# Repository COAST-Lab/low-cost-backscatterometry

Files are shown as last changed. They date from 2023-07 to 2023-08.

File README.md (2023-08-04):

# Documentation

•	The goal is to create a device that measures turbidity in a water sample.  Components include: Particle Argon microprocessor attached via stacking headers to an Adalogger FeatherWing (which includes a PCF 8523 RTC and SD card slot-note there must always be a battery in the coin battery holder, even if its a dead one, or the device will lose track of time), Adafruit AW9523 LED driver, Adafruit 7341 sensor, IR LED, cuvette holder, light blocking cap, 12.5mm x 12.5mm x 45mm (outer dimension) cuvette, and housing.  The LED and sensor must be perpindicular to each other, which the cuvette holder is designed to accomodate. Light from the LED enters the sample, and after striking any turbidity-causing particles in the water sample, bounces off and is read by the sensor.  The more light that reaches the sensor, the higher the turbidity.

•	The CAD file for the cuvette holder is in the CAD directory, and is called "cuvette holder v3", which is the most up-to-date version.  The light blocking cap that goes with it is in the same directory.  Directions for how to assemble the device are also in the same directory, and is called "Cuvette Holder Notes and Specifications".  If printing a new cuvette holder, be advised that the inside walls of the cavities may need to be sanded/shaved, or their intended pieces may not fit.

• The housing for the device will need to be ordered.

•	 To flash the LED, there is a program in the following directory: Firmware/Turbidity_Argon.  As of 4 Aug, 2023, there are two versions: Turbidity_v3 and Turbidity_v4.  Both flash an IR LED for a set time interval while bright, and flashes for a set time interval while dim.  We do not want the LED to turn off completely, which is why the LED needs to switch back and forth from bright to dim.  This is a workaround for the sensor reading negative values, which will display as “0”.  During each interval, the AS7341 will take light measurements and record them to an SD card, and it will say whether the reading was during a bright or a dim interval.

•	Turbidity_v3 is a workable code, but just needs to be fine-tuned and condensed (see next steps).  Turbidity_v4 is an attempt to correct the issues in turbidity_v3, but is less usable than Turbidity_v3, and is a work in progress.

•	If sample collection and readings are needed before Turbidity_v4 is complete, then use Turbidity_v3.  Despite the issues with that version, it has fewer issues and does everything that is needed.

•	If testing Turbidity_v3 or Turbidity_v4, you can cover the sensor when the light goes dim, and uncover when the light goes bright; this will reflect in the readings.

•	The ATIME is set to 59, and ASTEP is set to 599, and Gain is set to AS7341_GAIN_4X, per Bob Brewin’s recommendation.  Using the equation: integration time = (ATIME + 1) x (ASTEP+1) x 2.78 µs, this leads to an integration time of 100.08 ms.  Integration time is the amount of time the sensor measures light, and the gain is the sensitivity of the sensor.  

•	Be advised: When flashing the program at each of the gain settings, it will not save to the SD card as that gain, it will only save as a number that increases by 1 as you increase to the next gain setting.  For example, the .5 setting outputs/saves to SD card as 0, and just increases by 1 for the next setting up.  Here it is, formatted as (Gain setting -- what it saves to the card as):

    o	AS7341_GAIN_0_5x -- 0
  
    o	AS7341_GAIN_1x -- 1
    
    o	AS7341_GAIN_2x -- 2
    
    o	AS7341_GAIN_4x -- 3
    
    o	AS7341_GAIN_8x -- 4
    
    o	AS7341_GAIN_16x -- 5
    
    o	AS7341_GAIN_32x -- 6
    
    o	AS7341_GAIN_64x -- 7
    
    o	AS7341_GAIN_128x -- 8
    
    o	AS7341_GAIN_256x -- 9
    
    o	AS7341_GAIN_512x – 10

•	In the code, the LED intensities (bright and dim) are listed as variables, which are: LEDbright and LEDdim.  The bright setting is 250 and the dim setting is 1 (this is to clearly distinguish between the bright and dim settings).  These are arbitrary; feel free to adjust those numbers as needed when using the IR LED.  

• For both versions, the time stamp includes: year, month, day, hour, minute, second, and millisecond.  Be advised that this is not synced up with the RTC (the RTC cannot process units smaller than a second, while the Argon records the time since it was last reset in milliseconds), however it is useful to determine the timing of the intervals.  Also, in the code, be advised that the serial print and fileprint record the timestamps differently (HH:MM:SS.mmm and HH:MM:SS:mmm, respectively).  If you try to format the fileprint timestamp as HH:MM:SS.mmm, it will not record the hours for whatever reason.  

•	Optical measurements are complete.  This process involved placing the sensor in a box with a 1-inch diameter hole, with the sensor 5 inches away from the hole.  The inside of the box was black.  Outside of the box, there was a posterboard mounted at a 45 degree angle to the hole, and reflects light into the hole.  The following measurements were needed: while the posterboard was facing the sun (or flat on the ground) during a sunny day; shortly after the first measurement, but with a square or disk completely shadowing the posterboard; and indoors with the hole covered.  For light and shadow runs, two 1-minute runs were conducted and recorded, and for the dark, one 1-minute run was conducted.  Note that for the dark measurements, in order to get any reading at all, the gain had to be increased to x512, (which is the highest gain), and the integration time had to be increased to 1000 ms (this required the ATIME to be set to 103-the highest it’ll let you go, and an ASTEP of 3457).  Even then, we had to gradually let more and more light into the box by slowly removing the cover.  The measurements were averaged, and given to Alan Holmes for processing.  The measurements collected can be found in the following directory: Data_Analysis/Data/27Jul_Turbidity_Optical_Calibration_Data.xlsx.  Alan’s results are in: Data_Analysis/Data/WilmingtonResult-072723.xlsx (use the numbers in yellow). 

•	In addition to the runs above, there was an additional dark counts run, this time with enough light so that the average ADU for the NIR was ~100, per Alan’s recommendation.  This can be found in the same Data folder that the other optical files are in, and is named “100ADU_Dark_2023_Jul_28_1104.csv.

•	In the Firmware directory, there is a program called Hawkeyewavelengths-this just cycles the Argon’s onboard LED through all the wavelengths in the Hawkeye satellite.  Be advised that running this will move control of the Argon to the user, and it cannot be used for other applications unless control is returned to the Argon.  To return control to the Argon, simply flash the Returncontroltoargon program (be sure to flash while the on-board LED is on!).

# Next Steps

•	Condense the coding into functions.  Right now Turbidity_v4 is condensed into functions, but the timing is off-it’ll sometimes record bright intervals (250) as dim (1), and vice versa.  Also it stays on an interval for a lot longer.  Turbidity_v3 does not have functions and is bulkier, but does not have these issues either.

•	The number of consecutive samples at a given LED intensity appears to be variable. Sometimes it's two, sometimes four. We'd need that to be a fixed value for future analyses. Ideally a variable that can be set just like the intensity itself.  

•	Assemble the turbidity device.  The entire setup is on two breadboards connected together, but recommend finishing the coding before disassembly, since this setup already has a working RTC.

•	Order the housing for the turbidity device.

•	Once the turbidity meter is assembled, the next step is calibration.  Google ISO 7027 and EPA 180.1 for reference, as these are the standards to abide by.  

•	After calibration, the device will be ready to take measurements.

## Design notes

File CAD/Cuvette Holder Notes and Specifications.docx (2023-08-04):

Cuvette Holder, Version 3 Notes and Specifications

- Cuvette holder v2 is designed to hold a 12.5mm x 12.5mm x 45mm (outer dimensions) cuvette, with the AS7341 sensor, AW9523 LED driver, and Particle Argon/RTC combo mounted directly on the cuvette holder.
- The cavity that holds the cuvette is 30mm deep, leaving 15mm at the top to easily grab and swap out.
- The holes for the sensor and LED light are centered vertically and 15mm below the top of the cuvette holder.
- Place the AS7341 into the cavity with the same dimensions, with the sensor facing towards the inside of the cuvette holder, and text should be right side up. Note there is also a small notch in the upper right corner to accommodate the on-board LED. Also note there is a small portion around the center of the cavity that is raised-this surrounds the sensor and blocks out light coming from the LED.
- Place the AW9523 LED driver in the cavity with the same dimensions, with its main components on “top”, facing the user. The LED will need to be mounted on the “bottom” side of the LED driver (pinout 0), facing towards the inside of the cuvette holder. You may need to adjust the position of the LED in order to get it to fit. The large screw hole right above pinout 0 will need to be plugged up so it won’t let light through.
- The screw holes on the cuvette holder were left out, so the user has more flexibility on screw size, and can easily drill holes in the cuvette holder, or just tape or glue the parts to the cuvette holder. On the AS7341, the upper right corner should remain unscrewed, as it will get very close to the screw from the upper left corner screw of the LED driver.
- The cuvette holder is also designed to have a light blocking cap placed over the cuvette. This can be found in the same directory as the cuvette holder file.
- On one side of the cuvette holder are two grooves. Place the stacking headers from the Argon+RTC in the grooves, then secure to the cuvette holder, for example with electrical tape.
- Place the cuvette with sample water into the cuvette cavity, which is on the top of the cuvette holder.
- Place the light blocking cap over the cuvette and wiggle it in until snug.
- Note that the inside walls of the cavities may need to be sanded or shaved in order to accommodate their intended components.

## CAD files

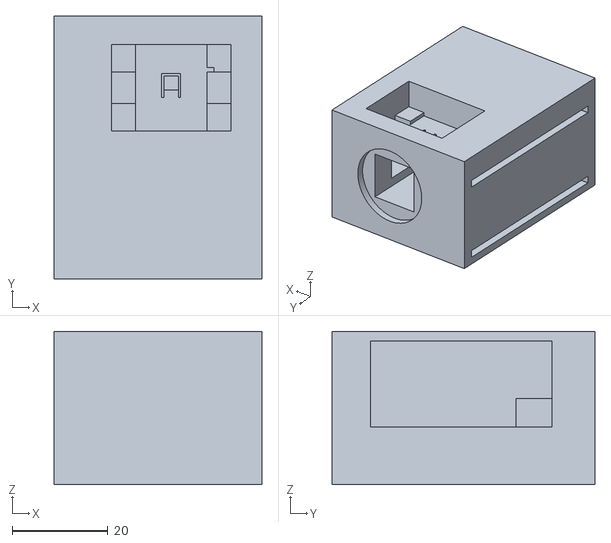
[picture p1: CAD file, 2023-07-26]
CAD/Cuvette Holder v3.stl
43.5 x 55.0 x 32.0

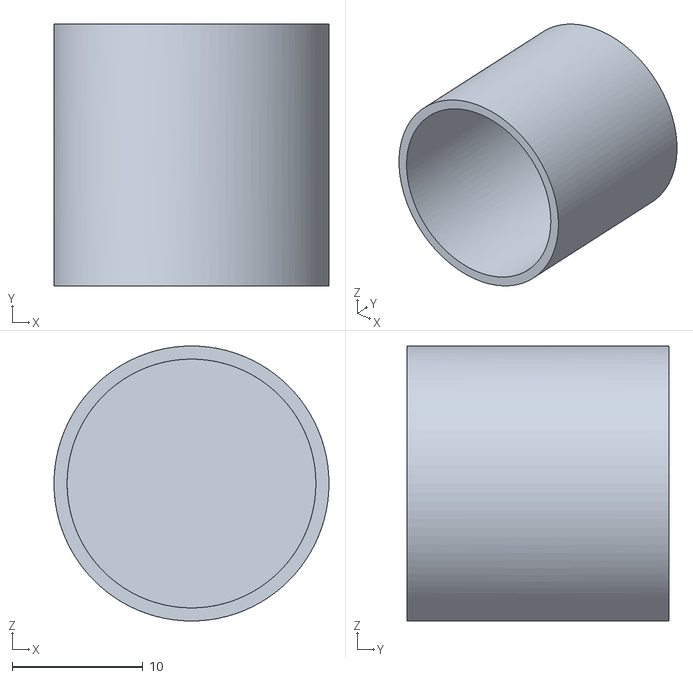
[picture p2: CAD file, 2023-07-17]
CAD/Light_Blocking_Cap.stl
21.0 x 20.0 x 21.0

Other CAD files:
CAD/Cuvette Holder v3.ipt
CAD/Light_Blocking_Cap.ipt

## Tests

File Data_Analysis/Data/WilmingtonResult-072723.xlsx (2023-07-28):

Wilmington Data of 7/27/20923
Alan Holmes
Gain was 4X
Integration time was 100 milliseconds
Measurements captured at 13:30 on Thursday July 27, 2023
74.69 | solar elevation angle in degrees
 |  |  |  | Expected | Derived
 |  |  |  | Sensor | Sensor
 |  |  |  | Irradiance | Calibration
 |  |  |  | in | in ADU Per | From
 | ADU | ADU | ADU | microwatts | microwatt | Data
 | AVERAGE | Shadow | Diff | per cm^2 | per cm^2 | Sheet
F1 415nm | 168.9791667 | 14.60416667 | 147.4166667 | 25.7 | 5.74 | 56.1 | (at gain of 512X) | (at 4X this would be 119th as much, or 0.47)
F2 445nm | 250.8125 | 19.77083333 | 220.5208333 | 29.0 | 7.59 |  | (and Tint of 100ms)
F3 480nm | 350.625 | 22.6875 | 310.6458333 | 47.4 | 6.56
F4 515nm | 434.5208333 | 25.8125 | 384.8958333 | 50.1 | 7.68
F5 555nm | 459.8333333 | 24.9375 | 410.1666666 | 50.8 | 8.08
F6 590nm | 514.25 | 25.79166667 | 461.5208333 | 51.2 | 9.02
F7 630nm | 681.1041667 | 30.83333333 | 614.4166666 | 65.3 | 9.41
F8 680nm | 669.6458333 | 31.8125 | 607.4583333 | 64.6 | 9.40
NIR | 698.8 | 52.25 | 643.6875 | 82.2 | 7.83 | 52 | (at gain of 128x) | (at 4X this would be 30.7th as much, or 1.69)
 |  |  |  | (From | (at 4X and 100 ms T-int)
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

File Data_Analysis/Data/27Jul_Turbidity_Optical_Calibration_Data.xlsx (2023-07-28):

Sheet: Light Measurements 1
Date | 2023/7/27 (Thursday)
ASTEP: | 599
ATIME: | 59
GAIN: | AS7341_GAIN_4X
INTEGRATION TIME: | 100.08 ms
APERATURE FACING: | 219° SW
 | Time | F1 415nm | F2 445nm | F3 480nm | F4 515nm | F5 555nm | F6 590nm | F7 630nm | F8 680nm | Clear | NIR
 | 13:27:20 | 169 | 251 | 351 | 435 | 461 | 516 | 684 | 672 | 2733 | 699
 | 13:27:21 | 170 | 252 | 352 | 436 | 461 | 516 | 684 | 672 | 2733 | 700
 | 13:27:22 | 170 | 252 | 352 | 436 | 462 | 516 | 684 | 673 | 2734 | 700
 | 13:27:24 | 169 | 251 | 352 | 436 | 461 | 515 | 683 | 672 | 2730 | 699
 | 13:27:25 | 169 | 251 | 351 | 436 | 461 | 516 | 683 | 672 | 2730 | 699
 | 13:27:26 | 169 | 251 | 351 | 435 | 461 | 516 | 683 | 672 | 2729 | 699
 | 13:27:27 | 169 | 251 | 352 | 436 | 462 | 516 | 684 | 672 | 2733 | 700
 | 13:27:29 | 170 | 252 | 352 | 436 | 461 | 515 | 683 | 671 | 2728 | 699
 | 13:27:30 | 170 | 252 | 352 | 436 | 462 | 516 | 684 | 672 | 2733 | 701
 | 13:27:31 | 170 | 252 | 352 | 437 | 462 | 517 | 685 | 673 | 2738 | 702
 | 13:27:33 | 170 | 252 | 352 | 436 | 462 | 517 | 685 | 674 | 2738 | 702
 | 13:27:34 | 170 | 252 | 353 | 437 | 462 | 517 | 685 | 673 | 2734 | 702
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

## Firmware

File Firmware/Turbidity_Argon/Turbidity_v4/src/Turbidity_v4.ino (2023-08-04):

//This program monitors light while giving a time stamp and recording both
//basic counts and raw values to an SD card

#include <Adafruit_AS7341.h>
#include <Adafruit_AW9523.h>
#include "RTClibrary.h"
#include <SdFat.h>

Adafruit_AS7341 as7341;
Adafruit_AW9523 aw;
RTC_PCF8523 rtc;
File myFile;
SdFat SD;

char daysOfTheWeek[7][12] = {"Sunday", "Monday", "Tuesday", "Wednesday", "Thursday", "Friday", "Saturday"};
const int SD_CHIP_SELECT = D5;
uint8_t LedPin = 0;
int LEDbright = 250;  // adjust this number as needed
int LEDdim = 1;       // adjust this number as needed

SYSTEM_THREAD(ENABLED);
SYSTEM_MODE(SEMI_AUTOMATIC);

void setup() {
  Serial.begin(9600);

  // Wait for communication with the host computer serial monitor
  while (!Serial) {
    delay(1);
  }
  
  if (!as7341.begin()){
    Serial.println("Could not find AS7341");
    while (1) { delay(10); }
  }
  
  // use ATIME of 103, ASTEP of 3457, and GAIN of 512x for dark counts during optical calibration
  as7341.setATIME(59);      
  as7341.setASTEP(599);
  as7341.setGain(AS7341_GAIN_4X);

  if (! rtc.begin()) {
    Serial.println("Couldn't find RTC");
    while (1);
  }

  if (! rtc.initialized()) {
    Serial.println("RTC is NOT running!");
    // following line sets the RTC to the date & time this sketch was compiled
    // rtc.adjust(DateTime(F(__DATE__), F(__TIME__)));
    // This line sets the RTC with an explicit date & time, for example to set
    // January 21, 2014 at 3am you would call:
    // rtc.adjust(DateTime(2014, 1, 21, 3, 0, 0));
  }

  if (! aw.begin(0x58)) {
    Serial.println("AW9523 not found? Check wiring!");
    while (1) delay(10);  // halt forever
  }

  Serial.println("AW9523 found!");
  aw.pinMode(LedPin, AW9523_LED_MODE);

  SD.begin(SD_CHIP_SELECT);
 
  File file = SD.open("data.csv", FILE_WRITE);

  if (file) {
    file.print("ASTEP:");
    file.print(',');
    file.println(as7341.getASTEP());
    file.print("ATIME:");
    file.print(',');
    file.println(as7341.getATIME());
    file.print("GAIN (check table):");
    file.print(',');
    file.println(as7341.getGain());
    // 0.5x records as 0, 1x records as 1, 2x records as 2, 4x records as 3, 
    // 8x records as 4, 16x records as 5, 32x records as 6, 64x records as 7,
    // 128x records as 8, 256x records as 9, 512x records as 10.
    file.println(" ");
    file.println("LED Intensity,Date,Time,Type,F1 (Basic),F2 (Basic),F3 (Basic),F4 (Basic),F5 (Basic),F6 (Basic),F7 (Basic),F8 (Basic),Clear (Basic),NIR (Basic),Type,F1 (Raw),F2 (Raw),F3 (Raw),F4 (Raw),F5 (Raw),F6 (Raw),F7 (Raw),F8 (Raw),Clear (Raw),NIR (Raw)"); // Headers
    file.close();
  } else {
    Serial.println(F("Error opening file!"));
  }
}

void loop() {


  // put your main code here, to run repeatedly:

  //File file = SD.open("data.csv", FILE_WRITE);
  //DateTime now = rtc.now();

  // Switch LED intensity to bright.

  unsigned long currentTime = millis();  // Current time in milliseconds
  unsigned long onTime = 500;  // 1 second on time
  unsigned long offTime = 500;  // 1 second off time

  // Calculate the time elapsed since the start of the loop
  unsigned long elapsedTime = currentTime % (onTime + offTime);



  bool isLedOn = (elapsedTime < onTime);
  aw.analogWrite(LedPin, isLedOn ? LEDbright : LEDdim); // Turn LED on or off
  // aw.analogWrite(LedPin, 250);

  //delay(100);

  serialprintresults();
  
  //save data to SD card

  // if (file) {

    //  print readings
     
    // file.print("LED BRIGHT");
  
    
    fileprintresults();
  // }

  // else {
  //  Serial.println(F("Error opening file!"));
  //}

  //delay(250);

//  Switch LED intensity to dim.



  bool isLedOff = (elapsedTime < offTime);
  aw.analogWrite(LedPin, isLedOff ? LEDdim : LEDbright);
  // aw.analogWrite(LedPin, 1);

  //delay(100);

  serialprintresults();
  
  //save data to SD card
  
  //if (file) {

    //  print readings
     
    //file.print("LED DIM");

  fileprintresults();



//else {
  //  Serial.println(F("Error opening file!"));
 // }

 // delay(250);

}

void serialprintresults() 
{

DateTime now = rtc.now();
unsigned long decimalseconds_to_record = (millis() % 1000)/1; //the divided by 1 has to stay, otherwise the program gets stuck during serial monitor!

Serial.print("LED INTENSITY:");
  Serial.print(" ");
  Serial.println(LEDbright);
  Serial.println();
  Serial.print(now.year(), DEC);
  Serial.print('/');
  Serial.print(now.month(), DEC);
  Serial.print('/');
  Serial.print(now.day(), DEC);
  Serial.print(" (");
  Serial.print(daysOfTheWeek[now.dayOfTheWeek()]);
  Serial.print(") ");
  Serial.print(now.hour(), DEC);
  Serial.print(':');
  Serial.print(now.minute(), DEC);
  Serial.print(':');
  Serial.print(now.second(), DEC);
  Serial.print('.');
  Serial.print(decimalseconds_to_record, DEC);
  Serial.println();

  uint16_t readings[12];
  float counts[12];

    if (!as7341.readAllChannels(readings)){
    Serial.println("Error reading all channels!");
    return;
  }

  for(uint8_t i = 0; i < 12; i++) {
    if(i == 4 || i == 5) continue;
    // we skip the first set of duplicate clear/NIR readings
    // (indices 4 and 5)
    counts[i] = as7341.toBasicCounts(readings[i]);
  }

  Serial.print("F1 415nm : ");
  Serial.print(counts[0]);
  Serial.print("  ");
  Serial.print("Raw Value : ");
  Serial.println(readings[0]);
  Serial.print("F2 445nm : ");
  Serial.print(counts[1]);
  Serial.print("  ");
  Serial.print("Raw Value : ");
  Serial.println(readings[1]);
  Serial.print("F3 480nm : ");
  Serial.print(counts[2]);
  Serial.print("  ");
  Serial.print("Raw Value : ");
  Serial.println(readings[2]);
  Serial.print("F4 515nm : ");
  Serial.print(counts[3]);
  Serial.print("  ");
  Serial.print("Raw Value : ");
  Serial.println(readings[3]);
  Serial.print("F5 555nm : ");

  // again, we skip the duplicates  

  Serial.print(counts[6]);
  Serial.print("  ");
  Serial.print("Raw Value : ");
  Serial.println(readings[6]);
  Serial.print("F6 590nm : ");
  Serial.print(counts[7]);
  Serial.print("  ");
  Serial.print("Raw Value : ");
  Serial.println(readings[7]);
  Serial.print("F7 630nm : ");
  Serial.print(counts[8]);
  Serial.print("  ");
  Serial.print("Raw Value : ");
  Serial.println(readings[8]);
  Serial.print("F8 680nm : ");
  Serial.print(counts[9]);
  Serial.print("  ");
  Serial.print("Raw Value : ");
  Serial.println(readings[9]);
  Serial.print("Clear    : ");
  Serial.print(counts[10]);
  Serial.print("  ");
  Serial.print("Raw Value : ");
  Serial.println(readings[10]);
  Serial.print("NIR      : ");
  Serial.print(counts[11]);
  Serial.print("  ");
  Serial.print("Raw Value : ");
  Serial.println(readings[11]);
  Serial.print("  ");
  Serial.println();
}

void fileprintresults() 
{

File file = SD.open("data.csv", FILE_WRITE);
DateTime now = rtc.now();
unsigned long decimalseconds_to_record = (millis() % 1000)/1; //the divided by 1 has to stay, otherwise the program gets stuck during serial monitor!

 uint16_t readings[12];
  float counts[12];

    if (!as7341.readAllChannels(readings)){
    Serial.println("Error reading all channels!");
    return;
  }

  for(uint8_t i = 0; i < 12; i++) {
    if(i == 4 || i == 5) continue;
    // we skip the first set of duplicate clear/NIR readings
    // (indices 4 and 5)
    counts[i] = as7341.toBasicCounts(readings[i]);
  }

if (file) {

  unsigned long currentTime = millis();  // Current time in milliseconds
  unsigned long onTime = 500;  // 1 second on time
  unsigned long offTime = 500;  // 1 second off time

  // Calculate the time elapsed since the start of the loop
  unsigned long elapsedTime = currentTime % (onTime + offTime);

  bool isLedOn = (elapsedTime < onTime);

  //delay(100);

  file.print(isLedOn ? LEDbright : LEDdim);
    file.print(',');
file.print(now.year(), DEC);
    file.print('/');
    file.print(now.month(), DEC);
    file.print('/');
    file.print(now.day(), DEC);
    file.print(" (");
    file.print(daysOfTheWeek[now.dayOfTheWeek()]);
    file.print(") ");
    file.print(',');
    file.print(now.hour(), DEC);
    file.print(':');
    file.print(now.minute(), DEC);
    file.print(':');
    file.print(now.second(), DEC);
    file.print(':');
    file.print(decimalseconds_to_record, DEC);
    file.print(',');
    file.print("BASIC COUNTS");
    file.print(',');
    file.print(counts[0]);
    file.print(',');
    file.print(counts[1]);
    file.print(',');
    file.print(counts[2]);
    file.print(',');
    file.print(counts[3]);
    file.print(',');
    file.print(counts[6]);
    file.print(',');
    file.print(counts[7]);
    file.print(',');
    file.print(counts[8]);
    file.print(',');
    file.print(counts[9]);
    file.print(',');
    file.print(counts[10]);
    file.print(',');
    file.print(counts[11]);
    file.print(',');
    file.print("RAW VALUES");
    file.print(',');
    file.print(readings[0]);
    file.print(',');
    file.print(readings[1]);
    file.print(',');
    file.print(readings[2]);
    file.print(',');
    file.print(readings[3]);
    file.print(',');
    file.print(readings[6]);
    file.print(',');
    file.print(readings[7]);
    file.print(',');
    file.print(readings[8]);
    file.print(',');
    file.print(readings[9]);
    file.print(',');
    file.print(readings[10]);
    file.print(',');
    file.println(readings[11]);
    file.close();

}

else {
    Serial.println(F("Error opening file!"));
  }

}

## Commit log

2023-06-26 Create Savetosdcard
    This program causes the AS 7341 to monitor, while printing the results and timestamp, then saving it to an SD card.
2023-07-13 Turbidity Raw Values and Basic Counts
    This is the code to run the turbidity sensor, which will collect data in both Raw Values and Basic Counts.
2023-07-13 Edited files
    [11Jul126pmData.csv, 11Jul135pmData.csv, 11Jul142pmData.csv, 11Jul154pmData.csv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]
2023-07-17 Uploading Additional Programs
    The Hawkeyewavelengths program causes the on-board LED on the Argon to cycle through various colors, while the sensor reads values. The Returncontroltoargon program needs to be flashed after flashing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
2023-07-18 Re-uploading cuvette holder version 2
    [Cuvette Holder 1cm.ipt, Cuvette Holder 1cm.stl, Cuvette Holder v2.ipt, Cuvette Holder v2.stl]
2023-07-19 Pushing Blackbox/Posterboard Readings
    These are the values collected for Dark, Light, and Shadow conditions for Turbidity (optical test).
    [2023_Jul_12_1005.csv, 2023_Jul_12_1035.csv, 2023_Jul_12_1044.csv, 2023_Jul_12_1052.csv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]
2023-07-20 Pushing July 20 Data
    [2023_Jul_20_1356.csv, 2023_Jul_20_1404.csv, 2023_Jul_20_1407.csv, 2023_Jul_20_1410.csv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]
2023-07-21 Pushing Jul 21 Data
    Adjusted gain and integration time and re-collected data.
    [2023_Jul_21_1212.csv, 2023_Jul_21_1219.csv, 2023_Jul_21_1221.csv, 2023_Jul_21_1224.csv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]
2023-07-26 Updated cuvette holder and dark counts w/new int time/gain
    [2023_Jul_24_0924.csv, Cuvette Holder v3.ipt, Cuvette Holder v3.stl]
2023-07-28 More Optical Calibration Data
    [11Jul126pmData.csv, 11Jul135pmData.csv, 11Jul142pmData.csv, 11Jul154pmData.csv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]
2023-08-02 Removing unnecessary files
    [Cuvette Holder v2.ipt, Cuvette Holder v2.stl, Cuvette Holder.ipt]
2023-08-02 Rearranging file locations
    [100ADU_Dark_2023_Jul_28_1104.csv, 27Jul_Turbidity_Optical_Calibration_Data.xlsx]
2023-08-04 Updated cuvette holder notes and specifications
